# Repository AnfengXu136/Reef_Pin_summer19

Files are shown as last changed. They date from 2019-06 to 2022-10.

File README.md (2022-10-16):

# D-SEA: The Depth-Sensor Enclosed Application
## Project Overview
### Abstract
Depth information is crucial in the creation of underwater 3D interactive models. Divers and researchers need depth measurements to accurately depict the structure and levels of underwater architectures for a virtual reality marine ecosystem. Currently, divers are manually measuring the depth using dive watches, but this method is inconsistent because of variable depth readings caused by changing wave heights and human errors.  To combat these problems, we created Depth-Sensor Enclosed Application (D-SEA) to automatically collect and average pressure data while displaying the calculated depth readings with values up to 30 meters underwater which is 3 times more than expected diving conditions. This device can be easily assembled with a cost of under one-hundred dollars.  Building from past developments, we are working on an affordable, waterproof prototype with a display that is readable underwater, an automatic transition between on and off states when submerged in seawater, and automatic data logging onto an SD card. From testing the recent prototype in a pool, results show that the D-SEA is able to accurately calculate the depth and display it on the screen.

### 100 Island Challenge
Our project falls within the greater context of the 100 Island Challenge, headed by the Scripps Institute of Oceanography. The 100 Island Challenge is a project that is collecting photographic, geographic, and oceanographic data in order to build models of coral reef communities around the world and track their changes in structure and growth over time. More information on the challenge can be found [here](http://100islandchallenge.org/).

### Requirements
Researchers from Scripps Institution of Oceanography wish to work with this device under the following conditions: Bring the device on a boat and turn it on before going diving with the corals. Then they dive down and place the devices on the coral reef, and the device starts collecting depth information and displaying it on the screen. The divers swim back and forth to do the photomosaic survey, capturing images of the devices and the data shown on the screen. After that, they collect the devices and return to the boat. They read the data from the devices and download it for backup. Finally, they turn off the device and charge the device overnight.

### Objectives
Based on the requirements from Scripps Institution of Oceanography, we are building a device that can measure and display depth information when it’s placed on coral reefs. Then the depth information could be captured by cameras and retrieved from images. The other detailed functions are described as follows.
* Switch: A switch is needed to make sure the device can turn on before diving and turn off when it’s back to land. 
* Waterproof: Since the device needs to be working under 10-15 meters of salt water for around 4 hours, it should be strictly waterproof to avoid erosion. Waterproof also means that there may not be any buttons or plugs on this device.
* Clear display: The device works in relatively shallow, high-illumination conditions in coral reef communities. There will be sunlight, wind, and wave changing over time. The display module should display the depth information as clear as possible under different conditions to make sure the information can be retrieved from the images accurately.
* Rechargeable: The device needs to be reusable and rechargeable. The battery needs to be working for around 4 hours and can be charged fully over one night.
* Data storage: There may be cases that researchers fail to retrieve accurate depth information from unclear images. For backup consideration, this device should be integrated with a data storage module such as an SD-card.

### Previous Work
GitHub repositories containing work done by the previous teams on this project can be found here. Their works and documentations provided us with valuable guidance for this project.
* [Summer 2018 REU](https://github.com/UCSD-E4E/coral-reef-mapping)
* [Spring 2019 Quarter](https://github.com/ChenLR/SIT)

## Team Members (Summer 2019 Engineers for Exploration)
* Anfeng Xu - UC San Diego
* Brian Sebastian - UC San Diego
* Charmaine Beluso - Mississippi State University
* Eamon Patamasing - UC San Diego

## Resources
* [User Manual](https://docs.google.com/document/d/1ufcVEwToTL347TIJa8BTdMBOQnbh-Dc6tYHnt09aWhc/edit?usp=sharing)
* [Final Report](https://docs.google.com/document/d/1GHIrqxifWv97SIiYkwtMFNrA6XIQ8vvvFCd0-GAbfDE/edit?usp=sharing)
* [Technical Paper]()
* [Final Presentation](https://docs.google.com/presentation/d/16IRXAvVATnhi6VliVaiazFm-Qb-JAyPtN_WVCFj1rOY/edit#slide=id.g3feb1946b7_17_0)
* [Notes for next team](https://docs.google.com/document/d/1U75X6sHqDsNa_K2ptZNxjGdgGvhvemMbGUb-xTKog6w/edit?usp=sharing)
* [Next steps](https://docs.google.com/document/d/1MVm5gGPROugtsDwmIqsRltZwrWXT1dNbkipjWg4ARCg/edit?usp=sharing)

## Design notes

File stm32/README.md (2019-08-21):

#  STM32f103c8t6

There are different versions of our code. Each version implements a new feature. More information about each version can be found under each version.
Our document only concerns v0.2, v0.2.1, and v0.3.

## Information about this Microcontroller

### MCU
Since last summer, students have developed different versions of D-SEA using multiple MCUs. Last summer (2018), the REU students used MSP430 for low power consumption. 
During the following academic year, student volunteers on the project were using Arduino because of its libraries for new features and fast software development. Last quarter (SP19), three students were using STM32 for a wide range of peripherals, power, and reliability. Though we do not need much MCU calculating power, we have decided to continue working on the STM32 version because the power consumption is not an issue, and it is cheap (5$), reliable, and flexible for software development.
* the datasheet can be found under "datasheet" folder

### IDE and Library
Our embedded software is fully dependant on STM32 Standard Peripheral Libraries since we are using a STM32 microcontroller. The SW4STM32R IDE (System Workbench for STM32) is free and does not have a limit on the memory of the program. It is compatible with both Windows and Mac, and it is based on Eclipse. We use ST-Link to download software into the embedded chip. With ST-Link and SW4, we can use step-by-step debugging. For basic components, we use GPIO, USART, I2C, SPI, ADC, EXTI, PWR, and RTC in STM32 Std Peripheral libraries. The driver code for each module is developed separately. Most of the breakout sensors are provided with Arduino libraries that can instantly plug in. Basically, we are rewriting these libraries with STM32 backend. Most of the user logic is defined in main.c file. The embedded software is modularized and extendable for future teams. To install the SW4STM32R IDE, click on the following link:
http://www.openstm32.org/System%2BWorkbench%2Bfor%2BSTM32
You need to create an account for the download.

Setting up the environment - after downloading SW4STM32 and cloning our repo, choose the version you want to open and open our project by clicking the cproject file. 
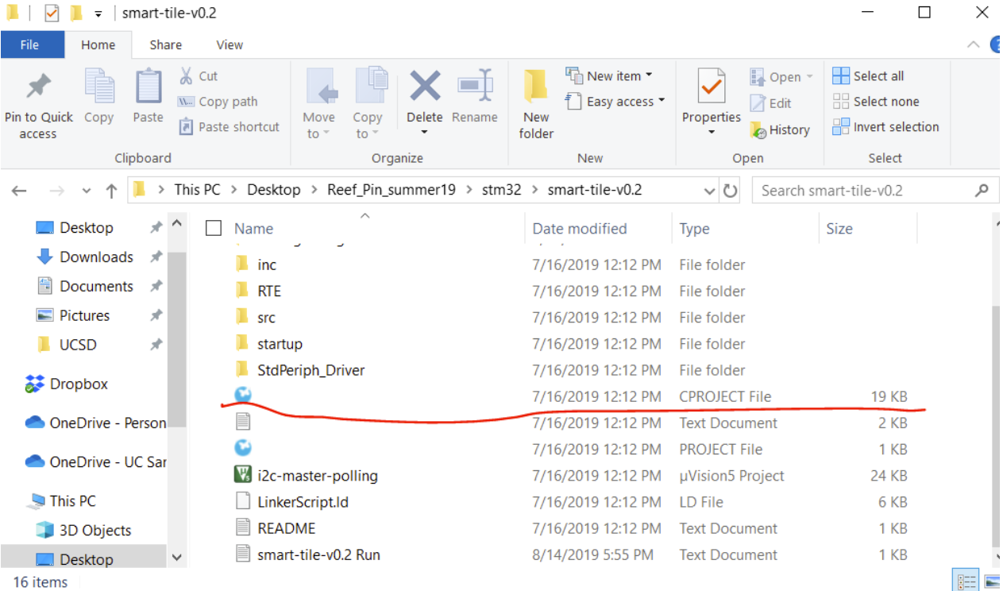
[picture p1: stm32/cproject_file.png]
cproject file


After opening the file, click “Run” and click again “Run Configuration.” This should open a window. 
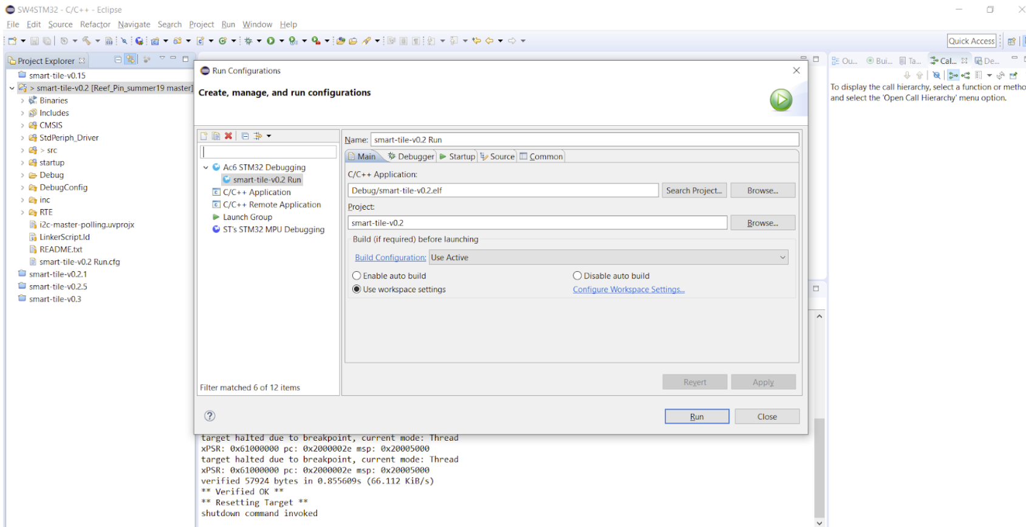
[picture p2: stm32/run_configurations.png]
run configurations


Then, go to “debugger” and change Reset Mode to “Software System Reset.”
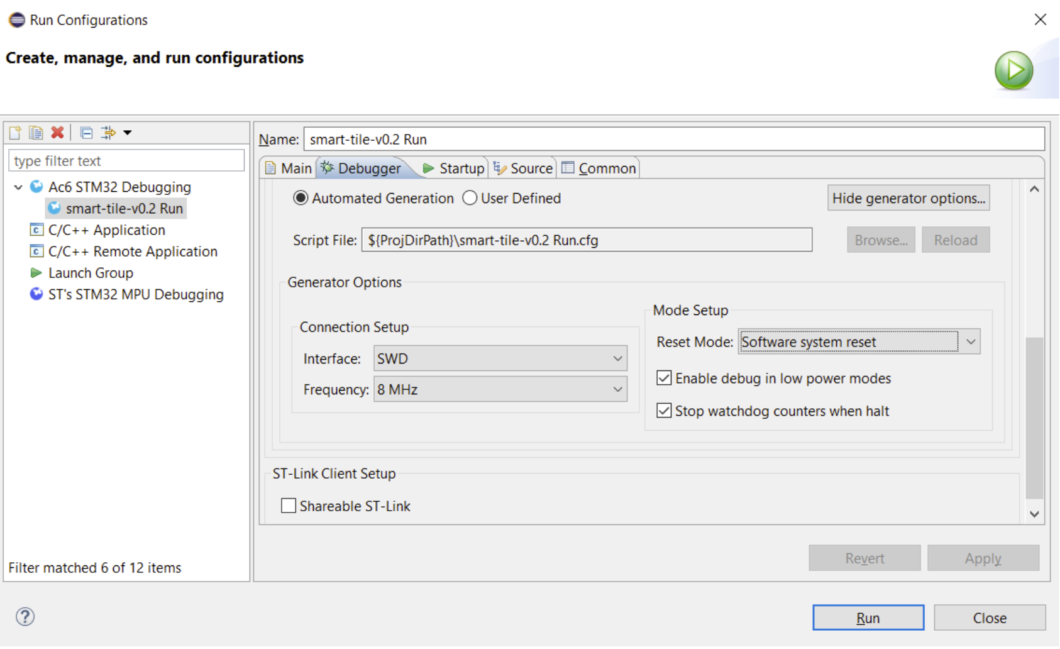
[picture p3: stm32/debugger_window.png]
debugger


Now, you should be able to code and upload your code.
To compile, click “build” and to upload the code, click “run.”

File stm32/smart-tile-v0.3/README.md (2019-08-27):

# smart-tile-v0.3

## Changes/Updates from v0.2.1

* Implemented 3 states: wet/standby/charging
* Changed wakeup/standby setting suited to wet/dry system: turn on when PA1 high and turn off when PA1 low
* Added charging state
* Changed the charging display
* Added turn on/off for LCD2
* Added water enable pin
* Disabled interrupt when in water. When in water, we do not want to use the wet/dry circutry because of the corrosion. Please disable the enable pin for wet/dry (something yet to be done). We have not developped the logistics to turn off the MCU when in water, but I believe you can either use depth information or turn on wet/dry circuit occationaly to check if it is on land.

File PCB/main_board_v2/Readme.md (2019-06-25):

## PCB files for main board
Includes Eagle files(a .sch and a .brd file), a schematic pdf and a lbr folder containing additional libraries. coral_power.lbr is a custom library file.

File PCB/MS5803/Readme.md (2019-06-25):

### PCB files for MS5803 Breakout design
A .sch, a .brd and a pcb Gerber zip file are included.

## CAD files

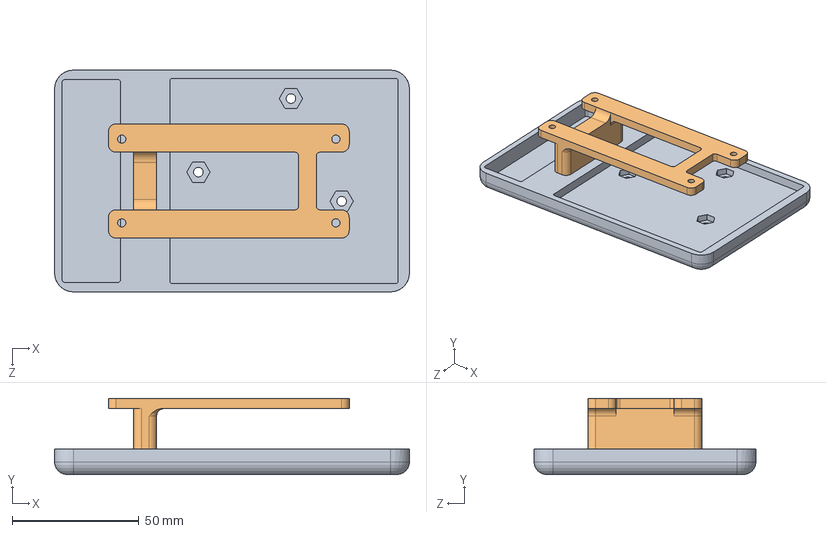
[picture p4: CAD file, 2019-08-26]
CAD/full_box_mount.SLDASM
140.0 x 30.0 x 87.5 mm
pcb_enclose
e-ink support

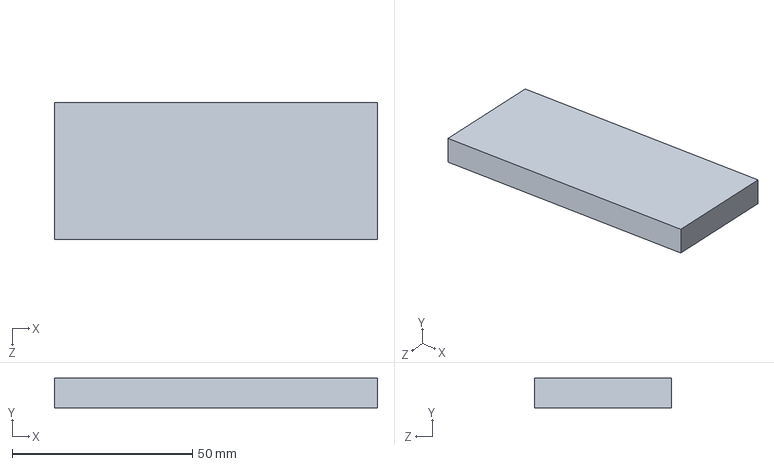
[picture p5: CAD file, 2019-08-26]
CAD/e-ink dummy.SLDPRT
89.6 x 8.30 x 38.0 mm

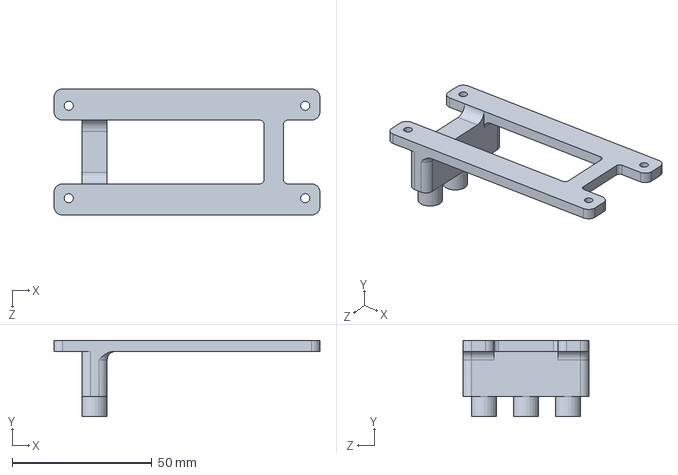
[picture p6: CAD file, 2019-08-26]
CAD/e-ink support.SLDPRT
95.0 x 27.3 x 45.0 mm

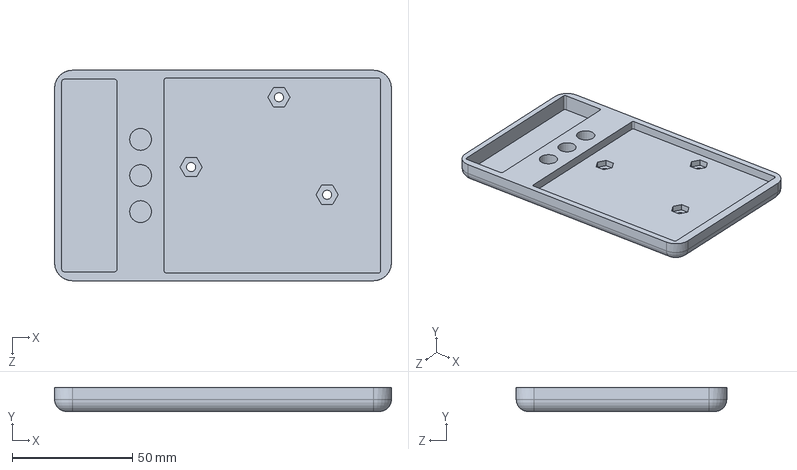
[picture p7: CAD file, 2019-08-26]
CAD/pcb_enclose.SLDPRT
140.0 x 10.0 x 87.5 mm

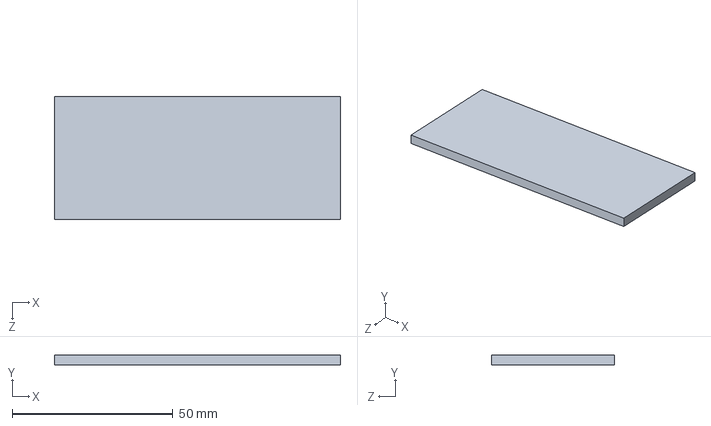
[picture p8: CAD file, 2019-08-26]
CAD/test acrylic.SLDPRT
88.9 x 3.17 x 38.1 mm

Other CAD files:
CAD/e-ink support.STL
CAD/pcb_enclose.STL

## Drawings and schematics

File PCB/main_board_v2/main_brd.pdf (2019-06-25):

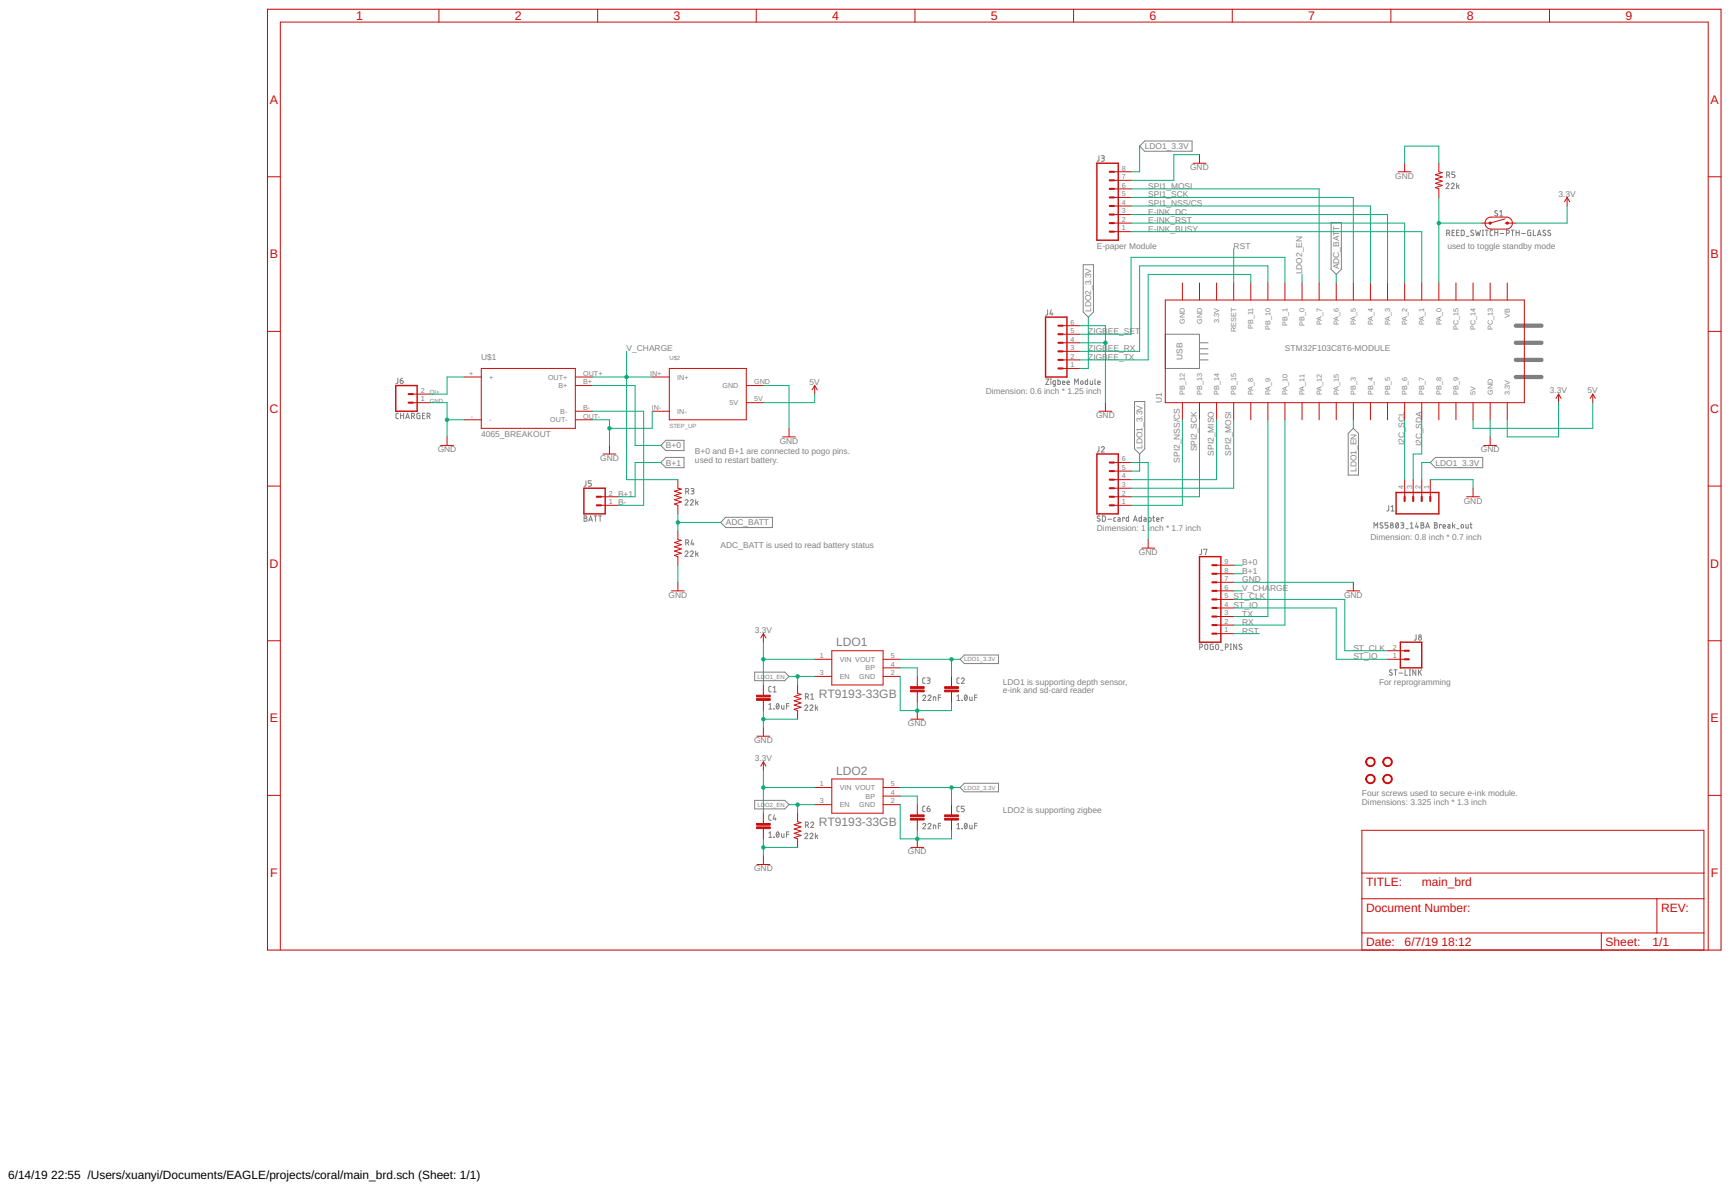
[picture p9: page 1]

B+0 and B+1 are connected to pogo pins. used to restart battery.

ADC_BATT is used to read battery status

6 5 ST_CLK

4 ST_IO
3 TX

e-ink and sd-card reader

Four screws used to secure e-ink module. Dimensions: 3.325 inch * 1.3 inch

Document Number: | REV:

Date: 6/7/19 18:12 | Sheet: 1/1

6/14/19 22:55 /Users/xuanyi/Documents/EAGLE/projects/coral/main_brd.sch (Sheet: 1/1)

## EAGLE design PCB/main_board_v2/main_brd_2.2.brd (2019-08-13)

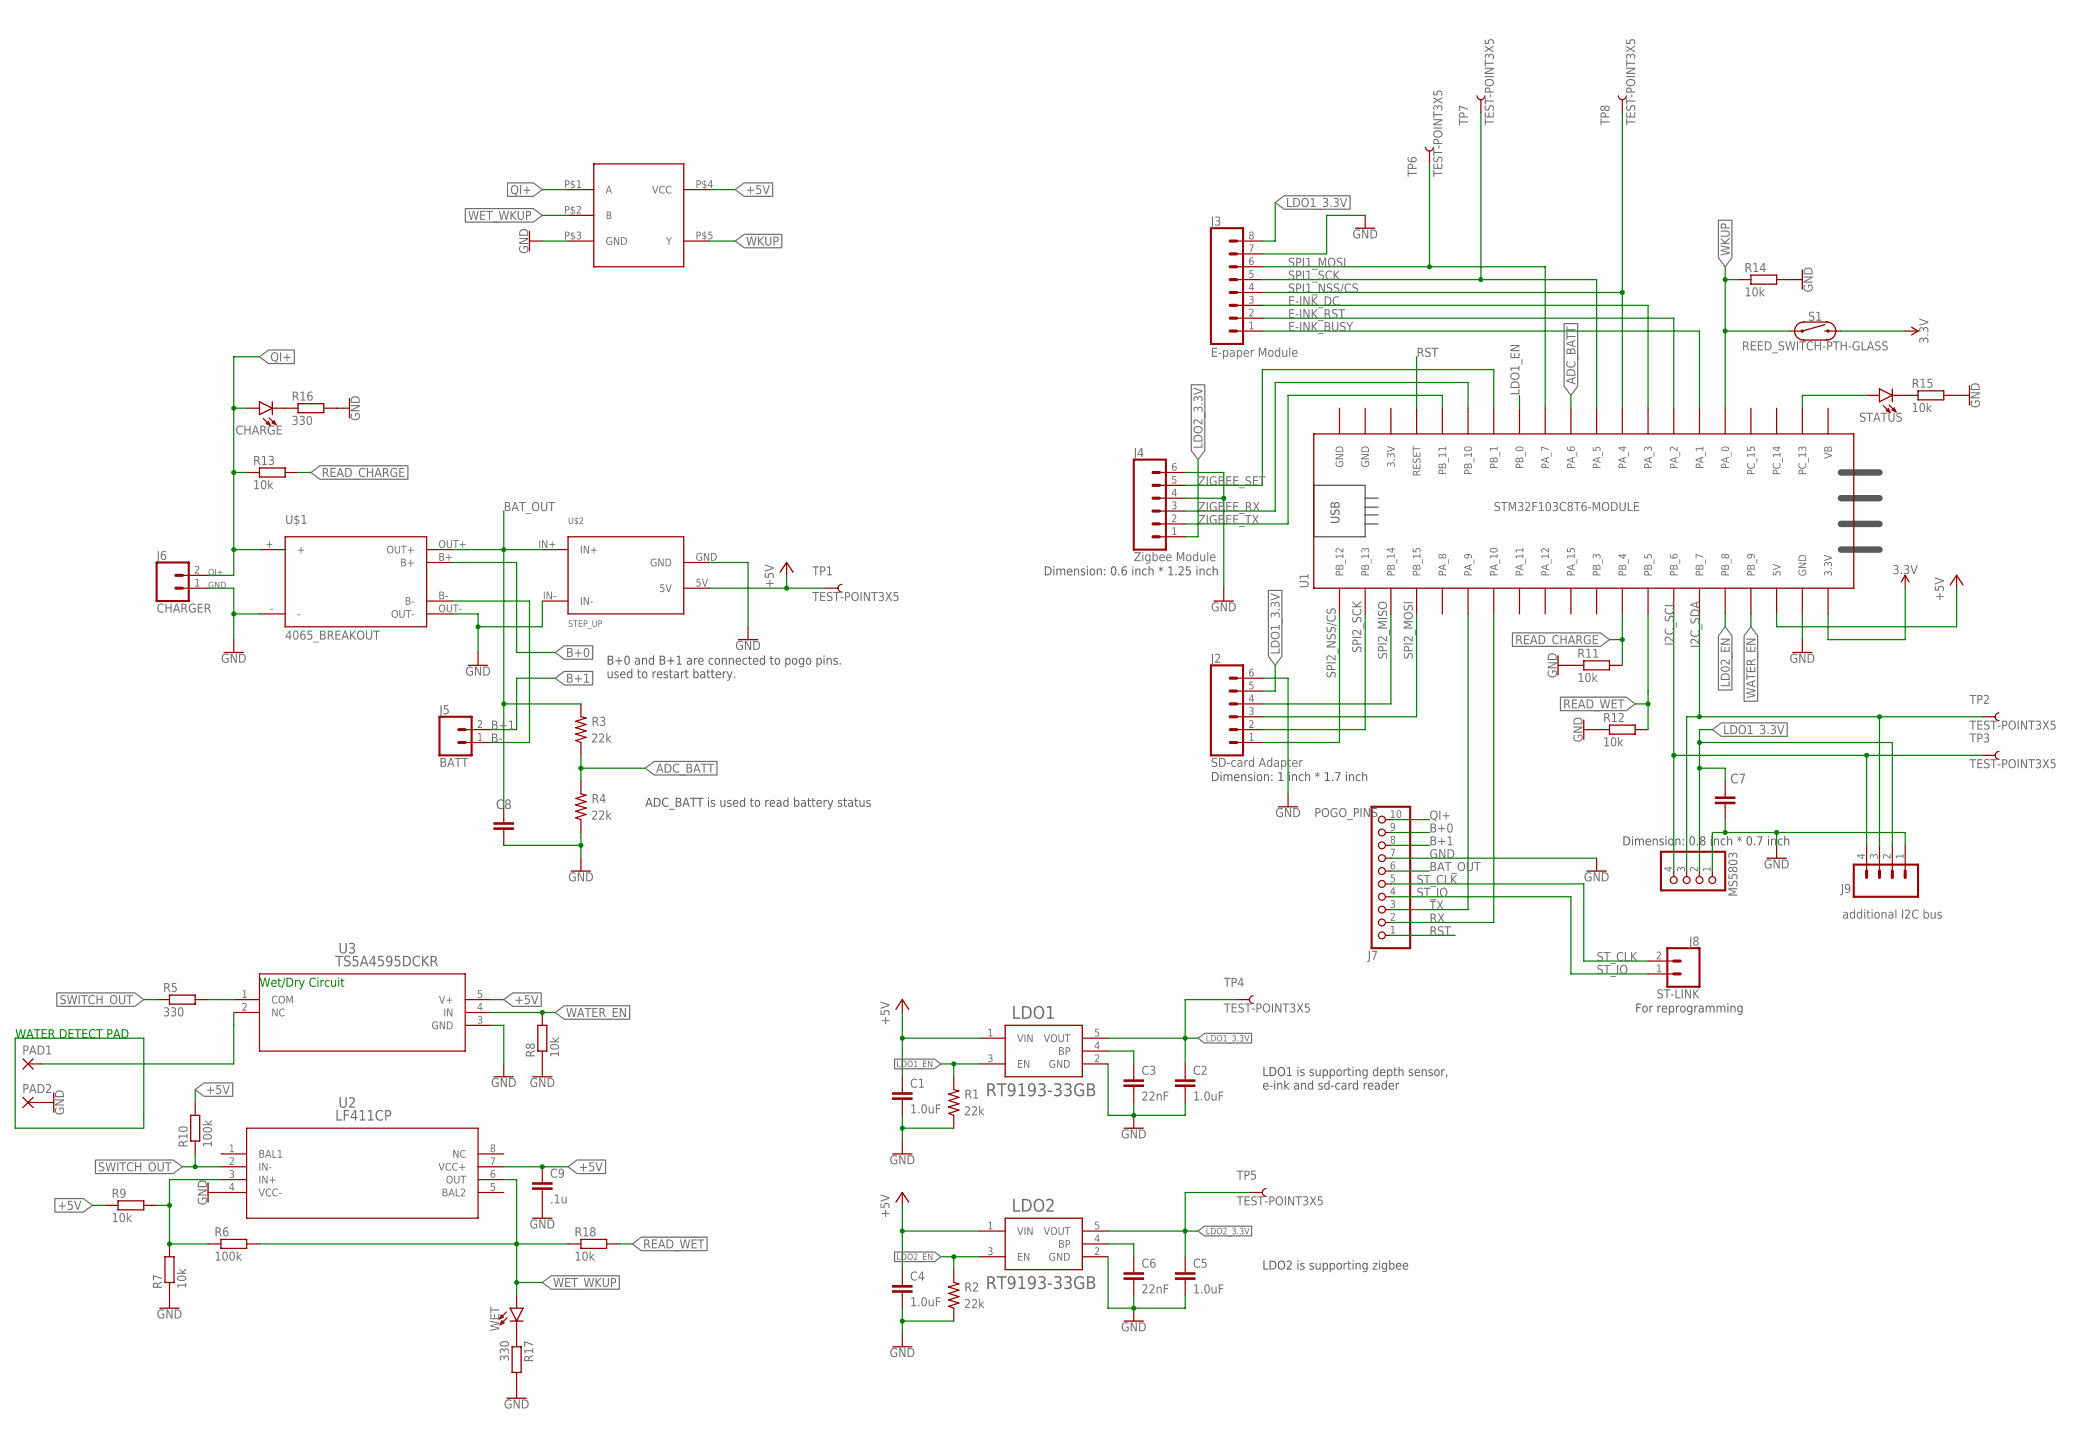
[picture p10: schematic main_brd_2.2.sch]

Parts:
C1, C2, C4, C5: 1.0uF; 0603
C3, C6: 22nF; 0603
C7: 100u; C025-050X050
C8: 220u; C025-050X050
C9: .1u; C0603
CHARGE: LED5MM; LED_5MM
J2: SD-card Adapter; 1X06
J3: E-paper Module; 1X08
J4: Zigbee Module; 1X06
J5: BATT; 1X02
J6: CHARGER; 1X02
J7: POGO_PINS; 1X10
J8: ST-LINK; 1X02
J9: additional I2C bus; 1X04
LDO1, LDO2: RT9193-33GB; SOT94P279X129-5N
MS5803: PINHD-1X4/90; 1X04/90
PAD1, PAD2: 3,81/1,4
R1, R2, R3, R4: 22k; 0603
R5, R16, R17: 330; R0603
R6, R10: 100k; R0603
R7, R8, R9, R11, R12, R13, R14, R15, R18: 10k; R0603
S1: REED_SWITCH-PTH-GLASS; REED_SWITCH_GLASS
STATUS: LED5MM; LED_5MM
TP1, TP2, TP3, TP4, TP5, TP6, TP7, TP8: TEST-POINT3X5; PAD.03X.05
U1: STM32F103C8T6-MODULE
U2: LF411CP; P8
U3: TS5A4595DCKR; DCK5
U$1: 4065_BREAKOUT; CHARGE_MODULE
U$2: STEP_UP; STEP_UP_99_69
U$3: 74LVC1G86SE-7; SOT25
WET: LED5MM; LED_5MM

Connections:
3.3V: S1.P$2 (2), U1.3.3V_1 (3.3V)
+5V: C1.1, C4.1, C9.1, LDO1.1 (VIN), LDO2.1 (VIN), R9.1, R10.2, TP1.P$1, U1.5V, U2.7 (VCC+), U3.5 (V+), U$2.5V, U$3.P$4 (VCC)
ADC_BATT: R3.1, R4.2, U1.PA_6
B+0: J7.9, U$1.B+
B+1: J5.2, J7.8
B-: J5.1, U$1.B-
BAT_OUT: C8.1, J7.6, R3.2, U$1.OUT+, U$2.IN+
E-INK_BUSY: J3.1, U1.PA_1
E-INK_DC: J3.3, U1.PA_3
E-INK_RST: J3.2, U1.PA_2
GND: C1.2, C2.2, C3.2, C4.2, C5.2, C6.2, C7.2, C8.2, C9.2, J2.6, J3.7, J4.4, J4.6, J6.1, J7.7, J9.1, LDO1.2 (GND), LDO2.2 (GND), MS5803.1, PAD2.1, R1.1, R2.1, R4.1, R7.1, R8.1, R11.1, R12.1, R14.2, R15.2, R16.2, R17.2, U1.GND_1 (GND), U1.GND_3 (GND), U2.4 (VCC-), U3.3 (GND), U$1.-, U$1.OUT-, U$2.GND, U$2.IN-, U$3.P$3 (GND)
I2C_SCL: J9.4, MS5803.4, TP3.P$1, U1.PB_6
I2C_SDA: J9.3, MS5803.3, TP2.P$1, U1.PB_7
LD02_EN: U1.PB_8
LDO1_3.3V: C2.1, C7.1, J2.5, J3.8, J9.2, LDO1.5 (VOUT), MS5803.2, TP4.P$1
LDO1_EN: LDO1.3 (EN), R1.2, U1.PB_0
LDO2_3.3V: C5.1, J4.1, LDO2.5 (VOUT), TP5.P$1
LDO2_EN: LDO2.3 (EN), R2.2
unnamed: C6.1, LDO2.4 (BP)
unnamed: C3.1, LDO1.4 (BP)
unnamed: CHARGE.K (C), R16.1
unnamed: R5.2, U3.1 (COM)
unnamed: R6.1, R7.2, R9.2, U2.3 (IN+)
unnamed: STATUS.A, U1.PC_13
unnamed: R15.1, STATUS.K (C)
unnamed: PAD1.1, U3.2 (NC)
unnamed: R17.1, WET.K (C)
QI+: CHARGE.A, J6.2, J7.10, R13.1, U$1.+, U$3.P$1 (A)
READ_CHARGE: R11.2, R13.2, U1.PB_4
READ_WET: R12.2, R18.2, U1.PB_5
RST: J7.1, U1.RESET
RX: J7.2, U1.PA_10
SPI1_MOSI: J3.6, TP6.P$1, U1.PA_7
SPI1_NSS/CS: J3.4, TP8.P$1, U1.PA_4
SPI1_SCK: J3.5, TP7.P$1, U1.PA_5
SPI2_MISO: J2.4, U1.PB_14
SPI2_MOSI: J2.3, U1.PB_15
SPI2_NSS/CS: J2.1, U1.PB_12
SPI2_SCK: J2.2, U1.PB_13
ST_CLK: J7.5, J8.2
ST_IO: J7.4, J8.1
SWITCH_OUT: R5.1, R10.1, U2.2 (IN-)
TX: J7.3, U1.PA_9
WATER_EN: R8.2, U1.PB_9, U3.4 (IN)
WET_WKUP: R6.2, R18.1, U2.6 (OUT), U$3.P$2 (B), WET.A
WKUP: R14.1, S1.P$1 (1), U1.PA_0, U$3.P$5 (Y)
ZIGBEE_RX: J4.3, U1.PB_10
ZIGBEE_SET: J4.5, U1.PB_1
ZIGBEE_TX: J4.2, U1.PB_11

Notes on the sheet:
E-paper Module
For reprogramming
LDO1 is supporting depth sensor, e-ink and sd-card reader
LDO2 is supporting zigbee
ADC_BATT is used to read battery status
B+0 and B+1 are connected to pogo pins. used to restart battery.
Dimension: 1 inch * 1.7 inch
Dimension: 0.8 inch * 0.7 inch
Dimension: 0.6 inch * 1.25 inch
Wet/Dry Circuit
WATER DETECT PAD

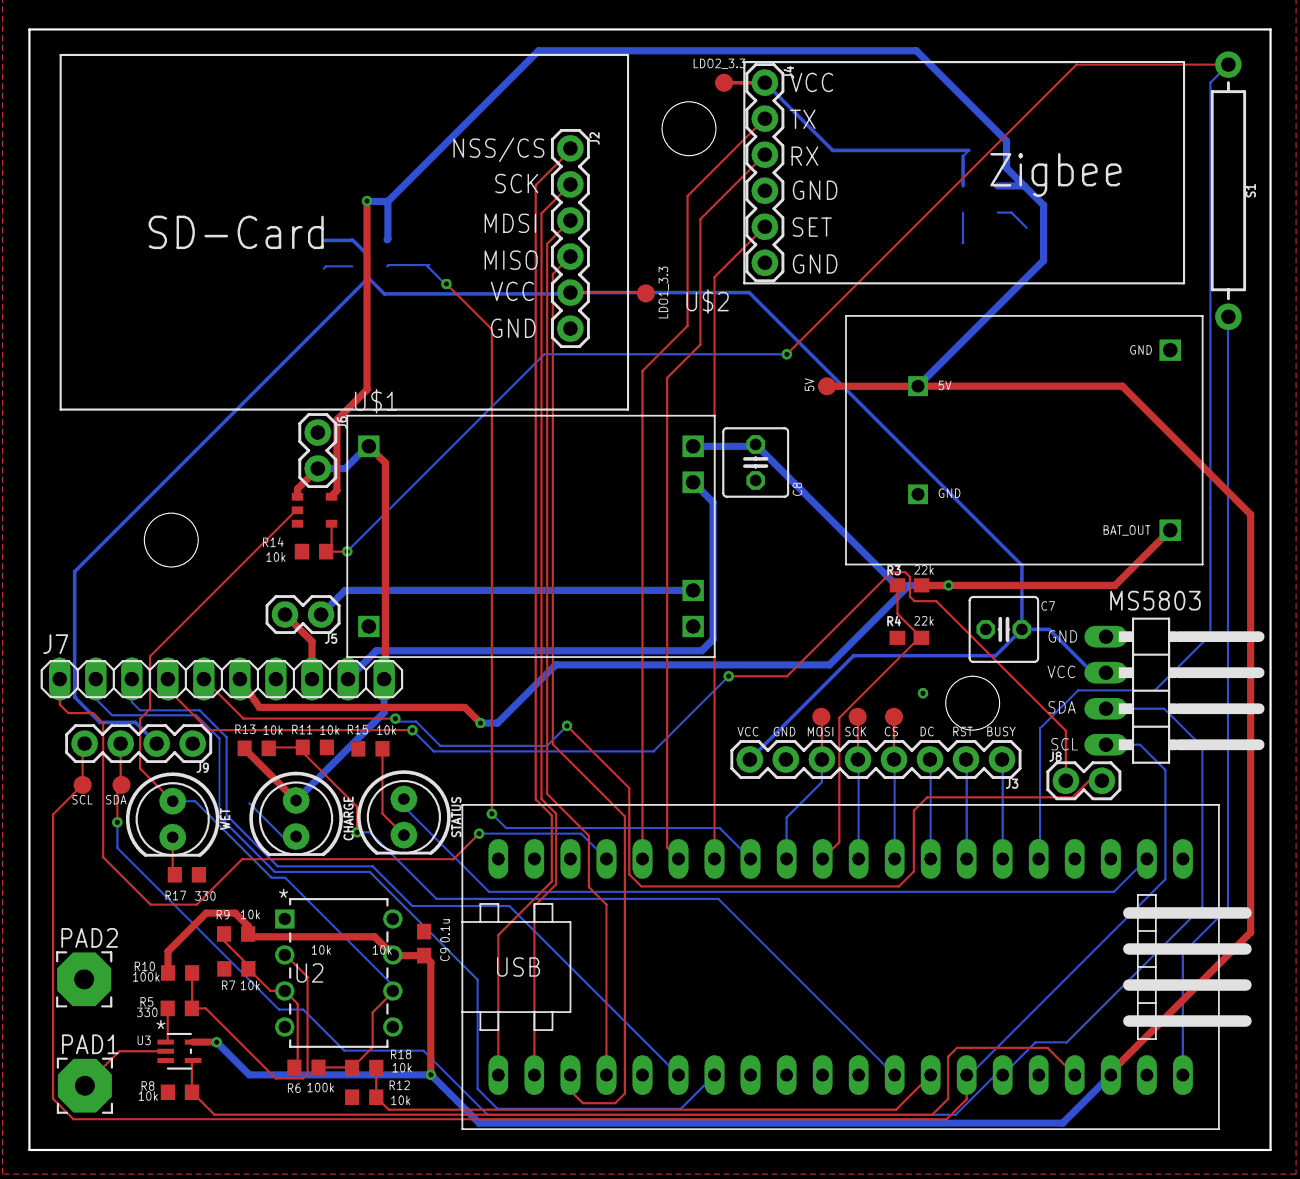
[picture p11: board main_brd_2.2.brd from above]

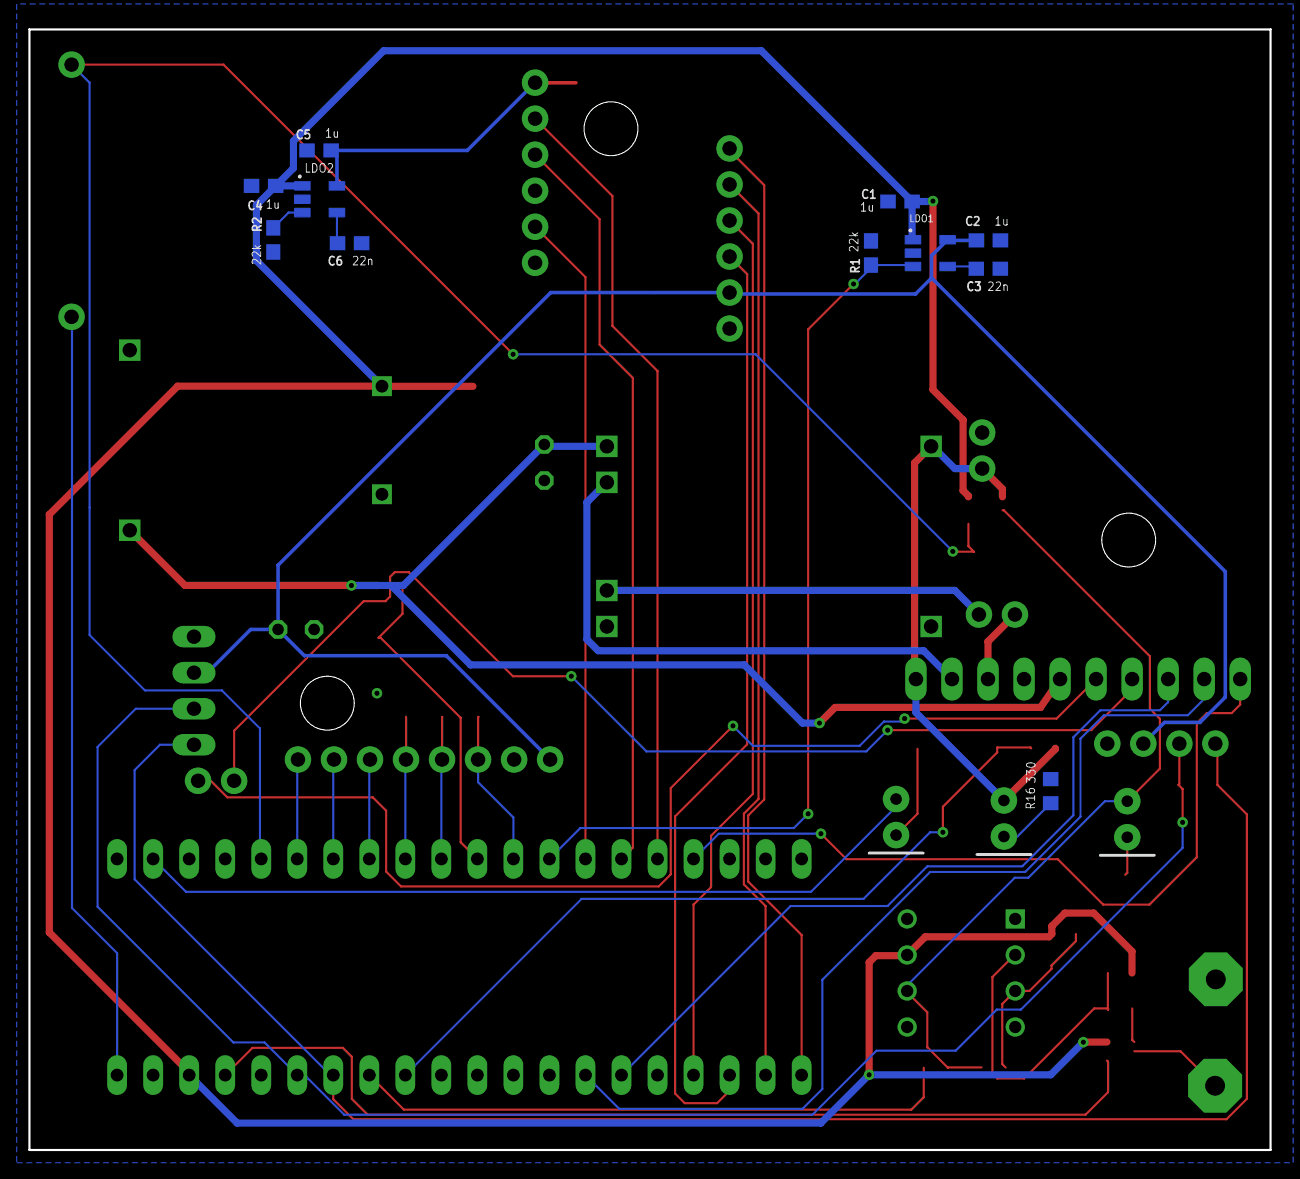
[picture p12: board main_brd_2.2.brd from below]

Board: 2 copper layers, 87.5 x 79.0 mm, 58 parts (11 on the bottom side), 48 nets.

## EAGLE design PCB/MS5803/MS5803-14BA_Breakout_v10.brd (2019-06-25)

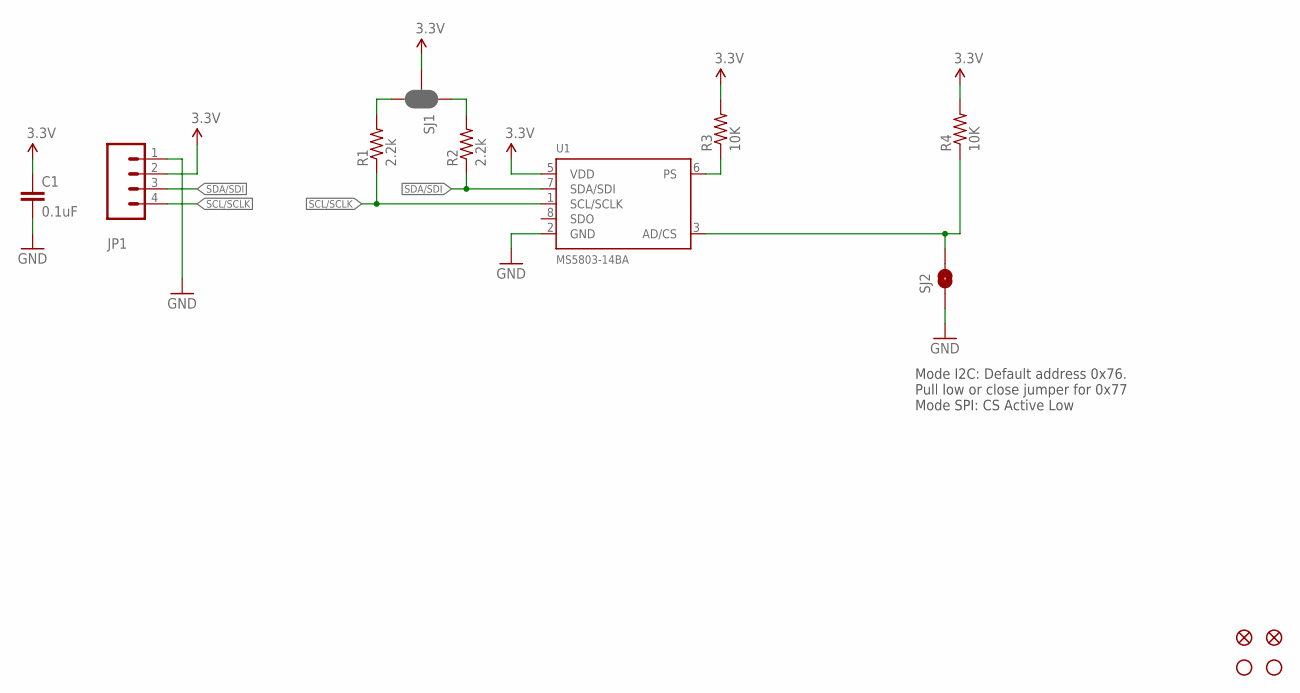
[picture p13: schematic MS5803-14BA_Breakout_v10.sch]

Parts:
C1: 0.1uF; 0603-CAP
FID1, FID2: FIDUCIAL1X2; FIDUCIAL-1X2
JP1: CONN_04PTH; 1X04
R1, R2: 2.2k; 0603-RES
R3, R4: 10K; 0603-RES
SJ1: JUMPER-PAD-3-NC_BY_PASTE; PAD-JUMPER-3-NC_BY_PASTE_YES_SILK_FULL_BOX
SJ2: SOLDERJUMPERNO; SJ_2S-NO
STANDOFF1, STANDOFF2: STAND-OFFTIGHT; STAND-OFF-TIGHT
U1: MS5803-14BA; MS5803

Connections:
3.3V: C1.1, JP1.2, R3.2, R4.2, SJ1.2, U1.5 (VDD)
AD/CS: R4.1, SJ2.2, U1.3 (AD/CS)
GND: C1.2, JP1.1, SJ2.1, U1.2 (GND)
unnamed: R1.2, SJ1.3
unnamed: R2.2, SJ1.1
PS: R3.1, U1.6 (PS)
SCL/SCLK: JP1.4, R1.1, U1.1 (SCL/SCLK)
SDA/SDI: JP1.3, R2.1, U1.7 (SDA/SDI)

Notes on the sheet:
Mode I2C: Default address 0x76. Pull low or close jumper for 0x77 Mode SPI: CS Active Low

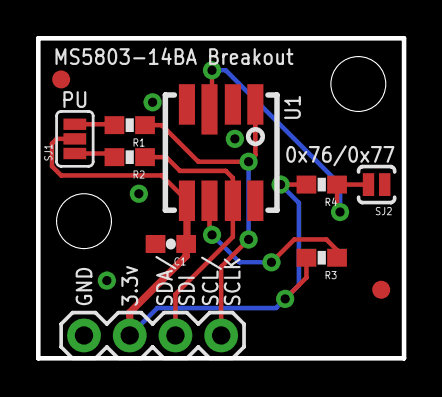
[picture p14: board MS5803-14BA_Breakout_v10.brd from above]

Board: 2 copper layers, 20.3 x 17.8 mm, 13 parts (0 on the bottom side), 8 nets.

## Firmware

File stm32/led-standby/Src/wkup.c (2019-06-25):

#include "wkup.h"
#include "delay.h"
#include "stm32f10x_gpio.h"
#include "stm32f10x_rcc.h"
#include "stm32f10x_pwr.h"
#include "stm32f10x_exti.h"

//1. In run mode, when PA0 occurs a rising edge, the interrupt routine of PA0 
//   will execute and check if pressing time is longer than 2s, then turn into standby mode.
//2. In standby mode, when PA0 occurs a rising edge, the program start from beginning. 
//   At the end of initialization, check if pressing time is longer than 2s, if not, back to standby mode,
//   otherwise, continue to run.


//Green LED indicates wakeup status. It holds green during Check_WKUP status. It blinks when application is running.
static uint8_t LED_Green_Status = 0;
void Init_LED_Green() {
	GPIO_InitTypeDef GPIO_InitStructure;
	// Set GPIO for LED 13
	// Enable clock for GPIOC
	RCC_APB2PeriphClockCmd(RCC_APB2Periph_GPIOC, ENABLE);
	// Configure PA13 as push-pull output
	GPIO_InitStructure.GPIO_Pin = GPIO_Pin_13;
	GPIO_InitStructure.GPIO_Speed = GPIO_Speed_2MHz;
	GPIO_InitStructure.GPIO_Mode = GPIO_Mode_Out_PP;
	GPIO_Init(GPIOC, &GPIO_InitStructure);
}

void Turn_On_LED_Green() {
	// Reset bit will turn on LED (because the logic is interved)
	GPIO_ResetBits(GPIOC, GPIO_Pin_13);
	LED_Green_Status = 1;
}

void Turn_Off_LED_Green() {
	// Set bit will turn off LED (because the logic is interved)
	GPIO_SetBits(GPIOC, GPIO_Pin_13);
	LED_Green_Status = 0;
}


void Toggle_LED_Green() {
	if(LED_Green_Status) {
		Turn_Off_LED_Green();
	}
	else {
		Turn_On_LED_Green();
	}
}


//enter standby mode
void Sys_Standby(void)
{  
	RCC_APB1PeriphClockCmd(RCC_APB1Periph_PWR, ENABLE);	//enable PWR clock
	PWR_WakeUpPinCmd(ENABLE);  //enable PA0 wakeup pin
	PWR_EnterSTANDBYMode();	  //enter standby mode 
}

void Sys_Enter_Standby(void)
{			 
	RCC_APB2PeriphResetCmd(0x01fc,DISABLE);//reset
	Sys_Standby();
}


//check if it is a real wakeup or noise	
uint8_t Check_WKUP(void) 
{
	uint8_t t=0;	//record time of pressing
	Turn_On_LED_Green(); // turn on LED green as indicator
	while(1)
	{ 
		if(GPIO_ReadInputDataBit(GPIOA,GPIO_Pin_0))
		{
			t++;			
			DelayMs(20);
			if(t>=100)		//press time is enough
			{
				//LED0=0;	 	
				return 1; 	
			}
		}else 
		{ 
			//LED0=1;
			return 0; 
		}
	}
}  


//PA0 interrupt
void EXTI0_IRQHandler(void)
{ 		    		    				     		    
	EXTI_ClearITPendingBit(EXTI_Line0); //clear interrupt  
	if(Check_WKUP())//check if it is a real turn off
	{		  
		Sys_Enter_Standby();  
	}
} 

//initialize wakeup module
void WKUP_Init(void)
{	
  GPIO_InitTypeDef GPIO_InitStructure;  		  
	NVIC_InitTypeDef NVIC_InitStructure;
	EXTI_InitTypeDef EXTI_InitStructure;
 
	RCC_APB2PeriphClockCmd(RCC_APB2Periph_GPIOA | RCC_APB2Periph_AFIO, ENABLE);
 
	//initialize gpio
	GPIO_InitStructure.GPIO_Pin =GPIO_Pin_0;	 
	GPIO_InitStructure.GPIO_Mode =GPIO_Mode_IPD;
	GPIO_Init(GPIOA, &GPIO_InitStructure);
	GPIO_EXTILineConfig(GPIO_PortSourceGPIOA, GPIO_PinSource0);	
 
	//initialize external interrupt
  EXTI_InitStructure.EXTI_Line = EXTI_Line0;	
	EXTI_InitStructure.EXTI_Mode = EXTI_Mode_Interrupt;			
	EXTI_InitStructure.EXTI_Trigger = EXTI_Trigger_Rising; //trigger at rising edge
  EXTI_InitStructure.EXTI_LineCmd = ENABLE;
	EXTI_Init(&EXTI_InitStructure);	
 
	// Set interrupt priority group
	NVIC_PriorityGroupConfig(NVIC_PriorityGroup_4);
	// Set System Timer IRQ at higher priority
	NVIC_SetPriority(SysTick_IRQn, 0);
	// Set PA0 priority
	NVIC_InitStructure.NVIC_IRQChannel = EXTI0_IRQn; 
	NVIC_InitStructure.NVIC_IRQChannelPreemptionPriority = 2; 
	NVIC_InitStructure.NVIC_IRQChannelCmd = ENABLE; 
	NVIC_Init(&NVIC_InitStructure);
	
	Init_LED_Green();
 
	if(Check_WKUP()==0) Sys_Standby(); //if not press 2s, still standby
		
}

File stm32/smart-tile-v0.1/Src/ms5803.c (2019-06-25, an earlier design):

/******************************************************************************
ms5803.cpp
Library for ms5803 pressure sensor.
Casey Kuhns @ SparkFun Electronics
6/26/2014
https://github.com/sparkfun/ms5803-14BA_Breakout

The MS58XX MS57XX and MS56XX by Measurement Specialties is a low cost I2C pressure
sensor.  This sensor can be used in weather stations and for altitude
estimations. It can also be used underwater for water depth measurements. 

In this file are the functions in the ms5803 class

Resources:
This library uses the Arduino Wire.h to complete I2C transactions.

Development environment specifics:
	IDE: Arduino 1.0.5
	Hardware Platform: Arduino Pro 3.3V/8MHz
	ms5803 Breakout Version: 1.0
	
**Updated for Arduino 1.6.4 5/2015**

This code is beerware. If you see me (or any other SparkFun employee) at the
local pub, and you've found our code helpful, please buy us a round!

Distributed as-is; no warranty is given.
******************************************************************************/

//#include <Wire.h> // Wire library is used for I2C
#include "delay.h"
#include "i2c.h"
#include "usart.h"

#include "ms5803.h"

#include <math.h>

enum ms5803_addr _address; 		// Variable used to store I2C device address.
uint16_t coefficient[8];// Coefficients;

int32_t _temperature_actual;
int32_t _pressure_actual;

void sendCommand(uint8_t command);	// General I2C send command function
uint32_t getADCconversion(enum measurement _measurement, enum precision _precision);	// Retrieve ADC result
void sensorWait(uint32_t time); // General delay function see: delay()


//------------------------------------------------
void ms5803_Init(enum ms5803_addr address) {
	i2c_init();
	_address = address;
	ms5803_Reset();
	ms5803_Begin();
}

void ms5803_Reset(void)// Reset device I2C
{
   sendCommand(CMD_RESET);
   sensorWait(3);
}

uint8_t ms5803_Begin(void)
// Initialize library for subsequent pressure measurements
{  
	uint8_t i;
	uint8_t buf[10];
	for(i = 0; i <= 7; i++)
  {
		uint8_t highByte; 
		uint8_t lowByte;
		sendCommand(CMD_PROM + (i * 2));
		i2c_read_multi_no_reg(_address, 2, buf);
		highByte = buf[0];
		lowByte = buf[1];
		coefficient[i] = (highByte << 8)|lowByte;
 	  // Uncomment below for debugging output.
		// USART2_PutChar('C');
		// USART2_PutInt(i);
		// USART2_PutString("= ");
		// USART2_PutInt(i);
		// USART2_PutInt(coefficient[i]);
		// USART2_PutString("\n");
	}

	return 0;
}
	
float ms5803_GetTemperature(enum temperature_units units, enum precision _precision)
// Return a temperature reading in either F or C.
{
	float temperature_reported;
	ms5803_GetMeasurements(_precision);
	// If Fahrenheit is selected return the temperature converted to F
	if(units == FAHRENHEIT)
  {
		temperature_reported = _temperature_actual / 100.0f;
		temperature_reported = (((temperature_reported) * 9) / 5) + 32;
		return temperature_reported;
	}
		
	// If Celsius is selected return the temperature converted to C	
	else
  {
		temperature_reported = _temperature_actual / 100.0f;
		return temperature_reported;
	}
}

float ms5803_GetPressure(enum precision _precision)
// Return a pressure reading units Pa.
{
	float pressure_reported;
	ms5803_GetMeasurements(_precision);
	pressure_reported = _pressure_actual;
	pressure_reported = pressure_reported / 10.0f;
	return pressure_reported;
}

void ms5803_GetMeasurements(enum precision _precision)

{
	//Retrieve ADC result
	int32_t temperature_raw = getADCconversion(TEMPERATURE, _precision);
	int32_t pressure_raw = getADCconversion(PRESSURE, _precision);
	
	
	//Create Variables for calculations
	int32_t temp_calc;
	int32_t pressure_calc;
	
	int32_t dT;
	
	//Now we have our first order Temperature, let's calculate the second order.
	int64_t T2, OFF2, SENS2, OFF, SENS; //working variables
		
	//Now that we have a raw temperature, let's compute our actual.
	dT = temperature_raw - ((int32_t)coefficient[5] << 8);
	temp_calc = (((int64_t)dT * coefficient[6]) >> 23) + 2000;
	
	// TODO TESTING  _temperature_actual = temp_calc;
	
	//Now we have our first order Temperature, let's calculate the second order.

	if (temp_calc < 2000) 
	// If temp_calc is below 20.0C
	{	
		T2 = 3 * (((int64_t)dT * dT) >> 33);
		OFF2 = 3 * ((temp_calc - 2000) * (temp_calc - 2000)) / 2;
		SENS2 = 5 * ((temp_calc - 2000) * (temp_calc - 2000)) / 8;
		
		if(temp_calc < -1500)
		// If temp_calc is below -15.0C 
		{
			OFF2 = OFF2 + 7 * ((temp_calc + 1500) * (temp_calc + 1500));
			SENS2 = SENS2 + 4 * ((temp_calc + 1500) * (temp_calc + 1500));
		}
    } 
	else
	// If temp_calc is above 20.0C
	{ 
		T2 = 7 * ((uint64_t)dT * dT)/pow(2,37);
		OFF2 = ((temp_calc - 2000) * (temp_calc - 2000)) / 16;
		SENS2 = 0;
	}
	
	// Now bring it all together to apply offsets 
	
	OFF = ((int64_t)coefficient[2] << 16) + (((coefficient[4] * (int64_t)dT)) >> 7);
	SENS = ((int64_t)coefficient[1] << 15) + (((coefficient[3] * (int64_t)dT)) >> 8);
	
	temp_calc = temp_calc - T2;
	OFF = OFF - OFF2;
	SENS = SENS - SENS2;

	// Now lets calculate the pressure
	

	pressure_calc = (((SENS * pressure_raw) / 2097152 ) - OFF) / 32768;
	
	_temperature_actual = temp_calc ;
	_pressure_actual = pressure_calc ; // 10;// pressure_calc;
	

}

uint32_t getADCconversion(enum measurement _measurement, enum precision _precision)
// Retrieve ADC measurement from the device.  
// Select measurement type and precision
{	
	uint32_t result;
	uint8_t highByte = 0, midByte = 0, lowByte = 0;
	uint8_t buf[3];
	
	sendCommand(CMD_ADC_CONV + _measurement + _precision);
	// Wait for conversion to complete
	sensorWait(1); //general delay
	switch( _precision )
	{ 
		case ADC_256 : sensorWait(1); break; 
		case ADC_512 : sensorWait(3); break; 
		case ADC_1024: sensorWait(4); break; 
		case ADC_2048: sensorWait(6); break; 
		case ADC_4096: sensorWait(10); break; 
	}	
	
	sendCommand(CMD_ADC_READ);
	i2c_read_multi_no_reg(_address, 3, buf);
	highByte = buf[0];
	midByte = buf[1];
	lowByte = buf[2];
	
	result = ((uint32_t)highByte << 16) + ((uint32_t)midByte << 8) + lowByte;

	return result;

}

//------------------------------------------------


void sendCommand(uint8_t command)
{	
	i2c_write_no_reg(_address, command);
	
}

void sensorWait(uint32_t time)
// Delay function.  This can be modified to work outside of Arduino based MCU's
{
	DelayMs(time);
}

//------------------------------------------------
void ms5803_demo() {
	float temp, pres;
	temp = ms5803_GetTemperature(CELSIUS, ADC_256);
	pres = ms5803_GetPressure(ADC_4096);
	printf("temp:\t%.3f\n", temp);
	printf("pressure:\t%.3f\n", pres);
}


float mbar_to_meter(float pressure) {
	// 1000 mbar = 1019.72 cm of water
	return pressure / 1000 * 10.1972;
}

static float init_pressure = 0;

float ms5803_getDepth() {
	float delta_pressure, depth;
	if (init_pressure == 0) init_pressure = ms5803_GetPressure(ADC_4096);
	delta_pressure = ms5803_GetPressure(ADC_4096) - init_pressure;
	depth = mbar_to_meter(delta_pressure);
	return depth;
}

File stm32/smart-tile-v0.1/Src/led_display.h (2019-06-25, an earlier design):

/*************************************************** 
  This is a library for our I2C LED Backpacks

  Designed specifically to work with the Adafruit LED Matrix backpacks 
  ----> http://www.adafruit.com/products/
  ----> http://www.adafruit.com/products/

  These displays use I2C to communicate, 2 pins are required to 
  interface. There are multiple selectable I2C addresses. For backpacks
  with 2 Address Select pins: 0x70, 0x71, 0x72 or 0x73. For backpacks
  with 3 Address Select pins: 0x70 thru 0x77

  Adafruit invests time and resources providing this open source code, 
  please support Adafruit and open-source hardware by purchasing 
  products from Adafruit!

  Written by Limor Fried/Ladyada for Adafruit Industries.  
  MIT license, all text above must be included in any redistribution
 ****************************************************/
#ifndef led_display_h
#define led_display_h

#include "stm32f10x.h"

#define LED_ADDR 0x70
#define LED_ON 1
#define LED_OFF 0

#define LED_RED 1
#define LED_YELLOW 2
#define LED_GREEN 3
 
#define HT16K33_BLINK_CMD 0x80
#define HT16K33_BLINK_DISPLAYON 0x01
#define HT16K33_BLINK_OFF 0
#define HT16K33_BLINK_2HZ  1
#define HT16K33_BLINK_1HZ  2
#define HT16K33_BLINK_HALFHZ  3

#define HT16K33_CMD_BRIGHTNESS 0xE0

#define SEVENSEG_DIGITS 5

typedef int boolean;
enum {false, true};

//this is the raw HT16K33 controller

void LED_7_Seg_Init(void);
void LED_7_Seg_Pre_Standby(void);
void LED_7_Seg_Standby(void);
void LED_7_Seg_SetBrightness(uint8_t b);
void LED_7_Seg_BlinkRate(uint8_t b);
void LED_7_Seg_WriteDisplay(void);
void LED_7_Seg_Clear(void);
void LED_7_Seg_Display(double n, uint8_t fracDigits, uint8_t base);
void LED_7_Seg_Demo(void);
void LED_7_Seg_Display_Depth(float depth);

// 7 segment
#define DEC 10
#define HEX 16
#define OCT 8
#define BIN 2

void writeDigitRaw(uint8_t x, uint8_t bitmask);
void writeDigitNum(uint8_t x, uint8_t num, boolean dot);
void writeColon(void);
void drawColon(boolean state);
void printFloat(double, uint8_t, uint8_t);
void printError(void);

#endif 

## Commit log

2019-06-25 coppied from SIT team
    [MS5803-14BA_Breakout_v10.brd, MS5803-14BA_Breakout_v10.sch, main_brd.brd, main_brd.sch]
2019-07-01 added I2C bus to the schematic and did the routing for the PCB board
    [main_brd.brd, main_brd.sch]
2019-07-02 updated board
    [main_brd.brd]
2019-07-05 finalized PCB and updated the Voltage reading methodology
    [main_brd.brd, main_brd.sch]
2019-07-12 new PCB version
    [main_brd.brd, main_brd.sch]
2019-07-12 added water enable pin
2019-07-24 Added PCB for version 3
    [main_brd_2.1.brd, main_brd_2.1.sch]
2019-08-09 Added version 2.2 of board
    [main_brd_2.2.brd, main_brd_2.2.sch]
2019-08-12 Created board 2.2
    [main_brd_2.2.brd, main_brd_2.2.sch]
2019-08-13 Fixed wkup and routing
    [main_brd_2.2.brd, main_brd_2.2.sch]
2019-08-23 Added CAD files for box mount
    [e-ink support.SLDPRT, e-ink support.STL, full_box_mount.SLDASM, pcb_enclose.SLDPRT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]
2019-08-23 Modified pin height
    [e-ink support.SLDPRT, e-ink support.STL, pcb_enclose.SLDPRT, pcb_enclose.STL]
2019-08-26 Fixed total height and tolerances
    [e-ink dummy.SLDPRT, e-ink support.SLDPRT, e-ink support.STL, full_box_mount.SLDASM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]

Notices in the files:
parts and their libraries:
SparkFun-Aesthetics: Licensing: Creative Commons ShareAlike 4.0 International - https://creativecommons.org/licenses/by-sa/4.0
